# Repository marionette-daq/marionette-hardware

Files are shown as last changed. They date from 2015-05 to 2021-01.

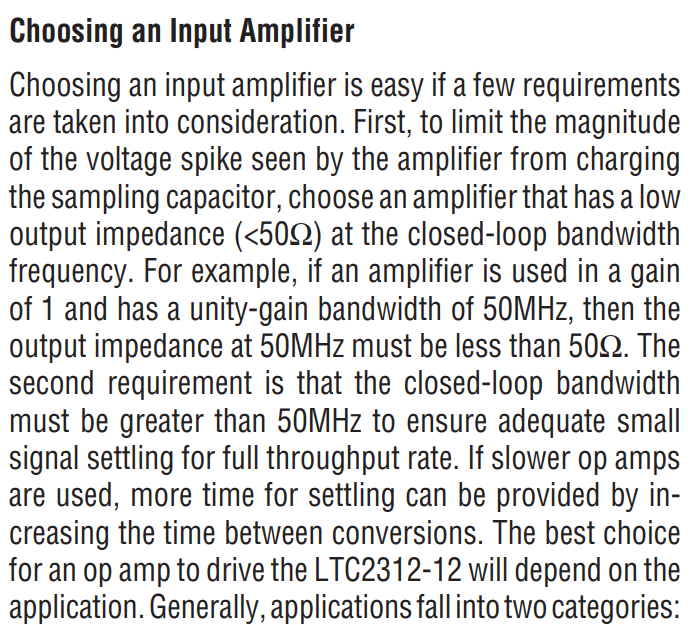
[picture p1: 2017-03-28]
current_amplifier/design/pictures/buffer_amp_requirements.png.png

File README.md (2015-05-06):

# Marionette Data Acquisition System

This repo contains the open source hardware used in the Marionette data acquisition system.
Click here to go to the [Wiki](https://github.com/marionette-daq/marionette-hardware/wiki)
## Marionette Specs

- TBD

## Marionette HW Description

Marionette provides these perifherals:

|Perifheral|Qty|
|---|---|
|GPIO|60|
|ADC|15|
|DAC|5|
|I2C|2|
|CAN 2.0B|1|
|SPI|1|
|SD Card|1|

## Other
* Board is designed in EAGLE 7.x and are fabricated using OSH Park's 4 layer service
* [BOM](https://github.com/marionette-daq/marionette-hardware/blob/master/mBOM.xlsx?raw=true) is available as an .XLSX file

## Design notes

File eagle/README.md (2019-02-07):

<h1 id="fab-header"> "Marionette" ("DK") PCB Manufacturing ("fab") Information </h1>
<h1 id="assembly-header"> APDM "Marionette" ("DK") PCB Assembly ("PCBA") Information </h1>

# Overview

### CURRENT PCB NAME AND VERSION: "DK-2.2"
### CURRENT PCBA NAME AND VERSION: "DK-2.2"

Ver   | Date       | Notes
------|------------|------------------------------------------------------------
2.0   | 2015-12-01 | Marionette V2.0 
2.1   | 2016.05.26 | Marionette V2.1 
2.2   | 2019.02.01 | Marionette V2.2 

## Description

The Marionette PCBA is 150 x 95 mm four layer PCB with a mix of through-hole
and SMT components on the top side.  

<h1 class="pdf" id="fab-pdf:fab" task="pdf:fab"/>

<h1 class="pdf" id="assembly-pdf:assembly" task="pdf:assembly"/>

<h1 id="assembly-images"> 
</h1>




Images of the Marionette v2.2

<h1 id="fab-info"> 
Printed Circuit Board (PCB) Fabrication information 
</h1>

- 4 layers, 1.59 mm (0.0625 inches) thick PCB 
- PCB bounding box size is 150 mm x 95 mm (5.9 x 3.74 inches)
- Minimum Trace / Space design rules
   - Outer layers: 0.15 mm (6.0 mil)
   - Inner layers: 0.2000 mm (7.8 mil)
- Outer dimension router tolerance: +/- 0.127 mm (0.005 in)
- Hole placement tolerance: .075 mm (+/-0.003 inch)
- Inner tab routed slot tolerance: +/- 0.127 mm (5 mil)
- Plated/Un-plated holes
  - There are 7 un-plated holes
  - There are 1304 plated through holes
  - PTH minimum diameter: 0.254 mm (10 mil)
  - PTH minimum annulus: 0.127 mm (5 mil) radius
- Plated slots
  - There 0 interior plated slots
- There are 3 fiducials
   - 3 on the top layer
- Panel tabs
   - Board does not yet have marked tabs. 
   - (Ignore for now) Do NOT place tabs anywhere else.
- Controlled impedance
   - While this board is no controlled impedance, the stackup is critical
     for performance of high speed signals (USB 2.0 high speed @ 480 Mbps)
- If not otherwise specified, build to IPC 6012 Class 2 or better.

## Materials

- Board thickness is 1.59 mm (0.063 inch) +/- 2 mil)
- Isola 370HR or equivalent
   - Laminate material MUST be Isola 370HR or equivalent (including an equivalent Dk).
   - Must have a flammability rating of at least V-0 (according to UL 94).
   - Must have a Dielectric Constant of ~ 4.5 at 1 MHz.
- Board Surface treatment should be ENIG, althogh immersion Silver is acceptable.
- White silkscreen on top and bottom surface
- Taiyo PSR-4000 or equivalent green soldermask on top and bottom

## Stack up

- Top and bottom prepreg thickness **MUST** be 0.111mm (4.4 mil) because of microstrips.

| Layer         | Thickness           | Notes                                        |
|---------------|---------------------|----------------------------------------------|
| Top Copper    | 0.043 mm /  1.7 mil |  Layer 1 foil, 1 oz Cu after plating         |
| prepreg       | 0.111 mm /  4.4 mil |  Prepreg Isola 370HR - 2x "1080"             |
| Layer 2       | 0.036 mm /  1.4 mil |  Layer 2 foil, 1 oz Cu                       |
| Core          | 1.207 mm / 47.5 mil |  Core Isola 370HR                            |
| Layer 3       | 0.036 mm /  1.4 mil |  Layer 3 foil, 1 oz Cu                       |
| prepreg       | 0.111 mm /  4.4 mil |  Prepreg Isola 370HR - 2x "1080"             |
| Bottom Copper | 0.043 mm /  1.7 mil |  Layer 4 foil, 1 oz copper after plating     |
| **Total Stackup** | **1.588 mm / 62.5 mil** |                                              |

## Array / Panel Information

- Coordinate with Contract Manufacturer (CM) for optimal size of this panel
- If no feedback from CM, then:
   - Panelize single board into apropriate sized array. Example: 5 x 3 array.
   - Use only "TAB" locations for attachment tabs
   - Use a ~ 6 mm (0.25 in) frame around the entire outside panel.

## Fabrication Files

### PCB Artwork

| Filename              | Notes                                         |
| --------------------- | --------------------------------------------- |
| marionette.outline.gbx      | RS274X file for the dimension (outline) layer |
| marionette.milling.gbx      | RS274X file for internal milling              |
| marionette.xln              | Excellon drill file                           |
| marionette.topsilk.gbx      | RS274X file for the top silkscreen            |
| marionette.topmask.gbx      | RS274X file for the top soldermask            |
| marionette.toplayer.gbx     | RS274X file for the top copper layer          |
| marionette.layer2.gbx       | RS274X file for the layer 2 copper            |
| marionette.layer3.gbx       | RS274X file for the layer 3 copper            |
| marionette.bottomlayer.gbx  | RS274X file for the bottom copper layer       |
| marionette.bottommask.gbx   | RS274X file for the bottom soldermask         |
| marionette.bottomsilk.gbx   | RS274X file for the bottom silkscreen         |

### Documentation

| Filename            | Notes                                   |
| ------------------- | --------------------------------------- |
| marionette.doc.gbx        | RS274X file for documentation           |
| marionette.ipc            | IPC-D-356 netlist and board layout file |

### Stencils

| Filename                 | Notes                                |
| ------------------------ | ------------------------------------ |
| marionette.toppaste.gbx        | RS274X file for solder paste stencil |

<h1 id="assembly-info">

Printed Circuit Board Assembly (PCBA) Information
</h1>

## Assembly info

- Assemble to IPC Class 2 or better
- Assemble with leaded solder 
- Aqueous flux and wash.
- There are 9 placements of 4 different components that require through hole soldering:
   - 6x Hirose ZX80-B-5SA microUSB vertical connectors (J5101 - J5106)
   - 1x CUI PJ-047AH 5.5mm x 2.1mm barrel power connector (J5001)
   - 1x Hirose ZX62D-B-5P8 USB micro connector (CF5101)
   - 1x FCI 73725-0110BLF USB Type-A vertical RA connector (J5107
- The J22 ZX62D-B-5P8 made by Hirose.  This is a hybrid through hole and SMT part.
**Beware solder ingress from J22 shield pins into the USB chamber.**
If there is solder ingress into the connector, please use a micro B USB
female connector to press into the J22 and clear the excess solder.

## Assembly Files

### Mounting location files

| Filename             | Description                                 |
| -------------------- | ------------------------------------------- |
| marionette.mnt    | Pick and place locations for components     |

### Standard netlist/layout files

Not ready yet

| Filename             | Description                             |
| -------------------- | --------------------------------------- |
| marionette.ipc         | IPC-D-356 netlist and board layout file |

### Stencils

| Filename                       | Notes                                |
| ------------------------------ | ------------------------------------ |
|     marionette.toppaste.gbx          | RS274X file for solder paste stencil |

### Bill of materials

There is the option of populating the 26 MHz clock with a TCXO or an XTAL
with associated filter networks.  The ATTRIBUTE: 'NO_MNT' indicates whether the
component should be populated.  

| Filename                    | Description                        |
| --------------------------- | ---------------------------------- |
| bom/marionette_bom.xls           | BOM with TCXO/XTAL population variants |

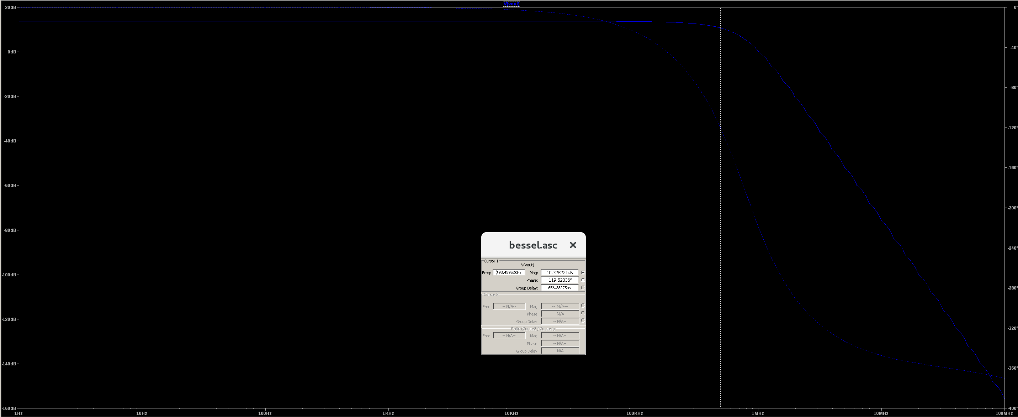
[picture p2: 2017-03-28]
current_amplifier/design/pictures/bessel_sim.png

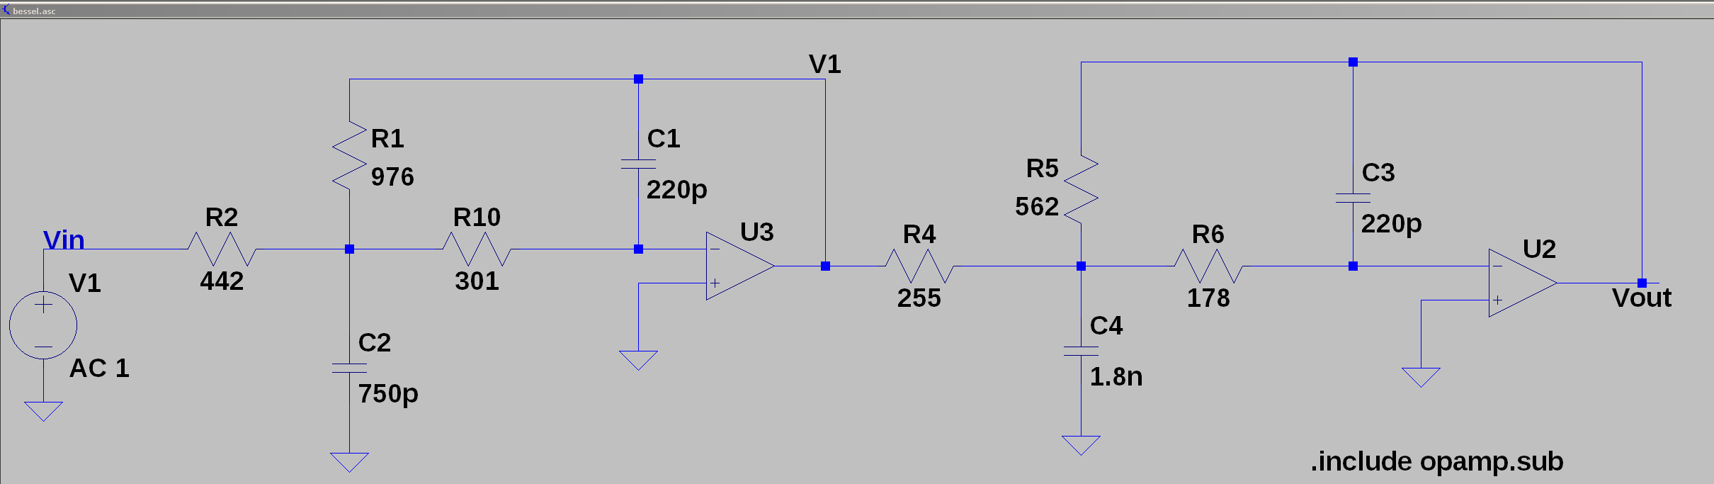
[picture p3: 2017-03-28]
current_amplifier/design/pictures/bessel_filter_lt.png

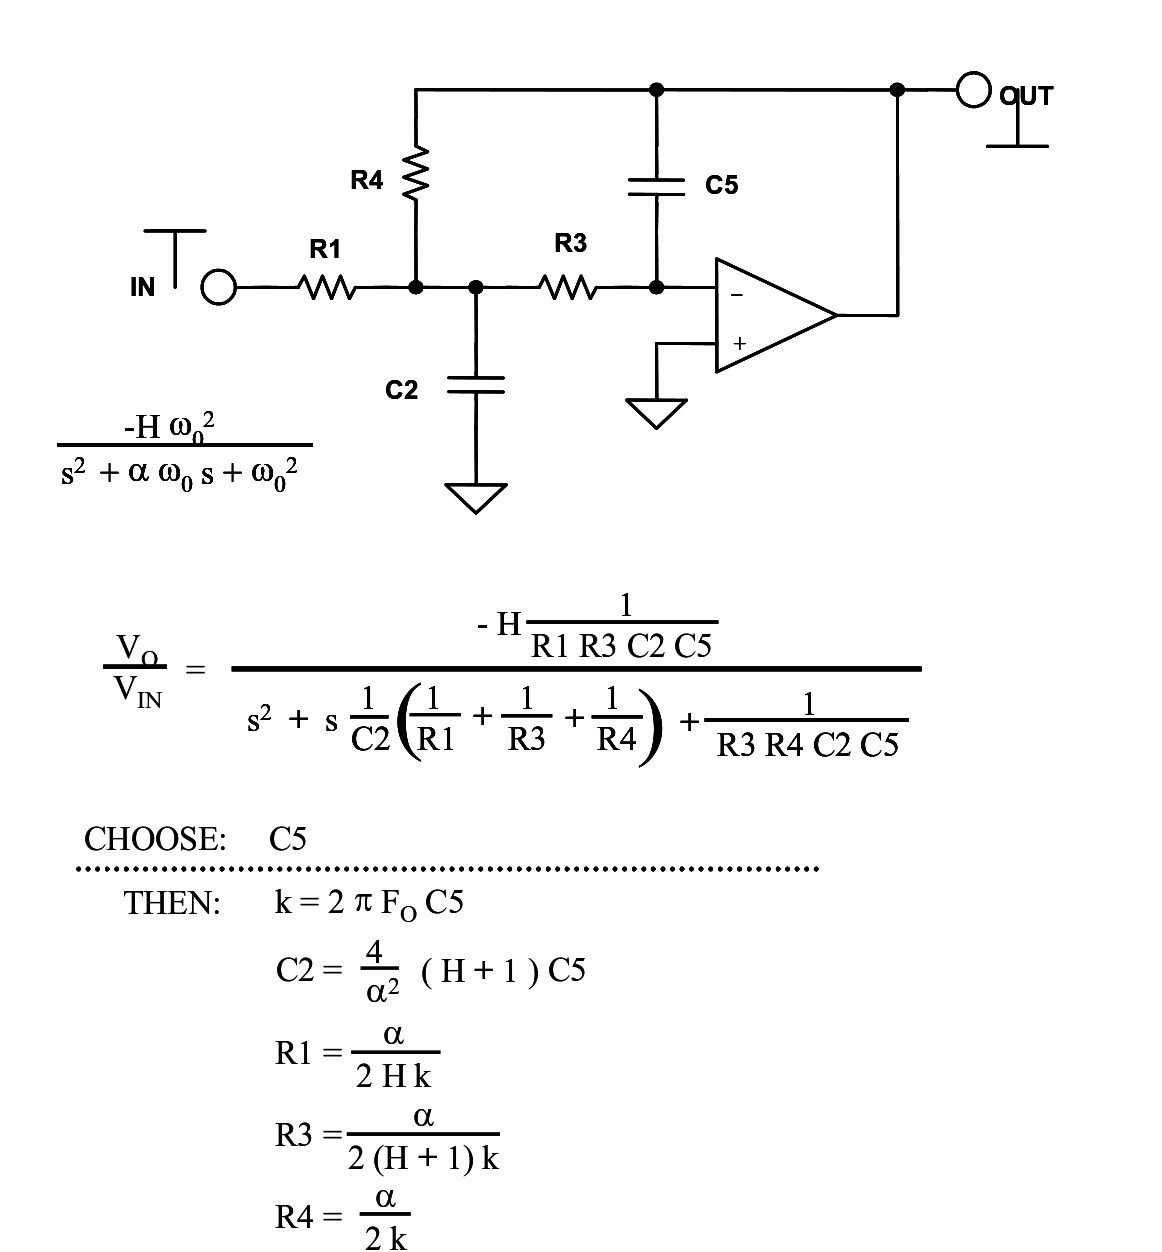
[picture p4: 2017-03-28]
current_amplifier/design/pictures/MFB.png

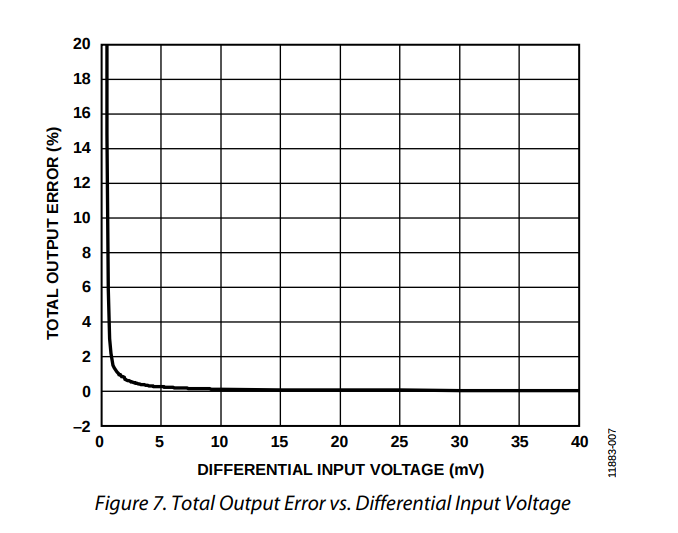
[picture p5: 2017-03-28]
current_amplifier/design/pictures/Error_vs_Diff_Input_Voltage.png

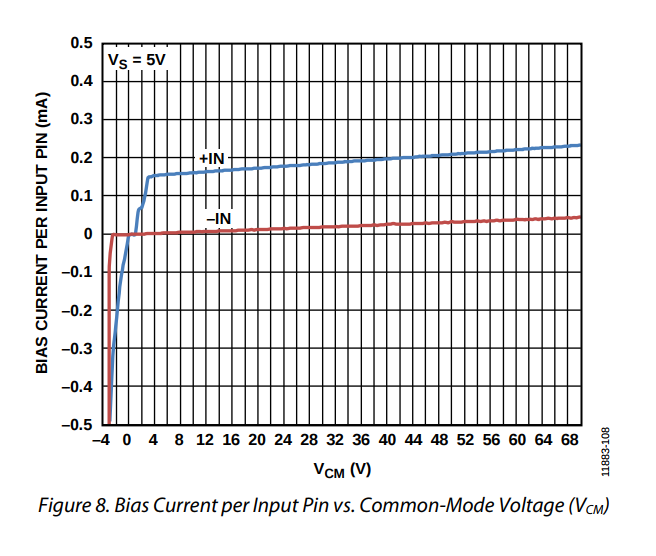
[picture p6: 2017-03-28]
current_amplifier/design/pictures/bias_current.png

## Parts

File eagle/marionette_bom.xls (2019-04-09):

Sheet: BOM
Bill Of Materials for Marionette
Modified: 2019.01.24
source file: marionette.sch
Variant: NA
PCB version 2.2
BOM revision 1
Cnt | REFs | Manf | PN | P/DNP (variant) | Desc | Vendor | Vendor-PN | Generic | Note
1 | C1 | Murata | GRM1555C1H6R8CA01D | P | Chip Capacitor, 6.8p, +-0.5pF, C0G/NP0, 50V, 0402 | Digikey | 490-5949-1-ND | Y
4 | C27, C30, C114, C154 | Murata | GRM1555C1H100JA01D | P | Chip Capacitor, 10p, +-5%, C0G/NP0, 50V, 0402 | Digikey | 490-5921-1-ND | Y
1 | C3 | Murata | GRM1555C1H330JA01D | P | Chip Capacitor, 33p, +-5%, C0G/NP0, 50V, 0402 | Digikey | 490-5936-1-ND | Y
1 | C42 | Murata | GRM1555C1H101JA01D | P | Chip capacitor, 100pF, 5%, 50V, C0G/NP0, 0402 | Digikey | 490-5922-1-ND | Y
30 | C50, C51, C52, C57, C59, C60, C61, C62, C63, C64, C67, C68, C69, C70, C71, C72, C75, C76, C77, C78, C79, C80, C49, C53, C54, C58, C65, C66, C73, C74 | Murata | GRM1555C1H102JA01D | P | Chip Capacitor, 1n, +-5%, 50V, C0G/NP0, 0402 | Digikey | 490-3244-1-ND | Y
6 | C29, C33, C101, C117, C142,C143 | Murata | GRM155R71E103KA01D | P | Chip capacitor, 10nF, 10%, 25V, X7R, 0402 | Digikey | 490-1312-1-ND | Y
1 | C33 | Murata | GRM155R71E103KA01D | P (XTAL/TCXO) | Chip capacitor, 10nF, 10%, 25V, X7R, 0402 | Digikey | 490-1312-1-ND | Y
2 | C41, C45 | TDK | CGA2B3X5R1H683K050BB | P | Chip capacitor, 68nF, 10%, 50V, X7R, 0402 | Digikey | 445-12211-1-ND | Y
43 | C2, C4, C7, C8, C9, C10, C11, C12, C13, C14, C15, C16, C17, C18, C19, C20, C21, C24, C25, C36, C37, C39, C43, C44, C47, C48, C86, C90, C91, C92, C97, C98, C99, C121, C126, C137, C140, C151, C152, C31, C103, C109, C110, C111 | Murata | GRM155R61E104KA87D | P | Chip capacitor, 100nF, 10%, 25V, X5R, 0402 | Digikey | 490-5920-1-ND | Y
3 | C40, C102, C113 | Walsin | 0402B104K500CT | P | Chip capacitor, 100nF, 10%, 50V, X7R, 0402 | Digikey | 1292-1176-1-ND | Y
10 | C23,C28,C32,C55,C56,C81,C82,C83,C85,C93 | Murata | GRM155R61A105KE15D | P | Chip capacitor, 1.0uF, 10%, 10V, X5R, 0402 | Digikey | 490-3890-1-ND | Y
21 | C5, C22, C26, C38, C87, C88, C89, C94, C96, C118, C120, C127, C138, C139, C145, C146, C153, C100, C104, C105, C112 | Murata | GRM21BR61E475KA12L | P | Chip Capacitor, 4.7u, 10%, 25V, X5R, 0805 | Digikey | 490-3335-1-ND | Y
5 | C46, C107, C108, C115, C116 | Murata | GRM21BR61H475KE51L | P | Chip Capacitor, 4.7u, 10%, 50V, X5R, 0805 | Digikey | 490-10751-1-ND | Y
1 | D3 | MCC | BAS40-TP | P | Schottky Diode, Vf = 1.0V, Vr = 40V, Imax = 200mA, SOT23-3 | Digikey | BAS40TPMSCT-ND | N
17 | D1,D2,D4,D5,D6,D7,D8,D9,D10,D11,D12,D13,D14,D15,D16,D17,D18 | Onsemi | ESD8006MUTAG | P | TVS protection Diode array, Vclamp = (5.5V, 8.4V), UDFN-8 3.3mm x 1.0mm | Digikey | ESD8006MUTAGOSCT-ND | N
4 | D20, D21, D22, D24 | Comchip | CDBA140SL-HF | P | Schottky Diode, Vr = 40V, Vf = 330mV, Imax = 1A DO-214AC/SMA | Digikey | 641-1762-1-ND | N
1 | D27 | Onsemi | MBRS260T3G | DNP | Schottky Diode, Vr = 60V, Imax = 2A, DO-214AA/SMB | Digikey | MBRS260T3GOSCT-ND | N | This diode is not required for most applications.
3 | D19, D25, D26 | Vishay | VSKY05201006-G4-08 | P | Schottky Diode, Vr = 20V, Imas = 500mA, 0402 package | Digikey | VSKY05201006-G4-08GICT-ND | N
1 | F1 | Bel Fuse | C1Q2 | P | Chip Fuse, 2A, 1206 | Digikey | 507-1080-1-ND | N
1 | J4 | JST | B2B-PH-K-S(LF)(SN) | P | JST 2 pin connector, 2A rating | Digikey | 455-1704-ND | N
1 | JP2 | Harwin | M20-9980445 | P | Header, 2 x 4, unshrouded, vert, TH, 100mil pitch | Digikey | 952-2122-ND | Y
3 | J3,J8,J9 | Sullins Connectivity | SBH11-PBPC-D20-ST-BK | P | IDC connector 40 pin, shrouded, keyed , 2 x 20 pin, 100mil | Digikey | S9175-ND | Y
1 | J5 | CUI | PJ-047AH | P | Jack, male, 5A, 16VDC, TH, Shielded, Internal Switch, (for 2.1mm pin Dia. 5.5mm hole dia. Plug) | Digikey | CP-047AH-ND | N
1 | J12 | Sullins Connectivity | SBH11-PBPC-D10-ST-BK | P | IDC connector 20 pin, shrouded, keyed, 2 x 10 pin, 100mil | Digikey | S9172-ND | Y
1 | J13 | CNC Tech | 3220-10-0300-00 | P | JTAG header, shrouded, keyed 2 x 5 pin. 50mil pitch | Digikey | 1175-1629-ND | Y
1 | J14 | Hirose | DM3D-SF | P | Micro SD card holder, push-pull manual extraction, no ejection mech. | Digikey | HR1941CT-ND | N
1 | J22 | Hirose | ZX-62D-B-5P8 | P | Connector, USB Micro B, surface mount + TH, RA | Digikey | H11610CT-ND | N
2 | JP1,JP5 | Sullins Connectivity | PRPC040SAAN-RC | DNP | Header, 1x2, male, breakaway, unshrouded, TH, 100mil 1 x 40: cut to 1x2 | Digikey | S1011EC-40-ND | Y
1 | JP3 | Sullins Connectivity | PRPC040SAAN-RC | P | Header, 1x3, male, breakaway, unshrouded, TH, 100mil 1 x 40: cut to 1x3 | Digikey | S1011EC-40-ND | Y
1 | JP9 | Sullins Connectivity | PRPC002DAAN-RC | P | Header, 2x2, male, unshrouded, TH, 100mil | Digikey | S2011EC-02-ND | Y
1 | J15 | Wurth | 398800302 | P | Euroterminal, 2 terminal, 5.08mm | Digikey | WM4393-ND | Y
1 | L1 | Murata | 1255AY-6R8M=P3 | P | Fixed Inductor, 6.8uH, Shielded, 3.4A, .043 ohms, 6.3mm x 6.3mm | Digikey | 490-14063-1-ND | N
1 | L2 | Bournes | SRN3015-2R2M | P | Fixed Inductor, shielded, 2.2uH, 20%, .072 ohms, 1.8A, 3.0mm x 3.0mm | Digikey | SRN3015-2R2MCT-ND | N
6 | LED1,LED2,LED3,LED4,LED6,LED8 | Wurth | 150060VS75000 | P | LED, Green, 20mA, diffused lens, 0603 | Digikey | 732-4980-1-ND | N
1 | LED5 | Rohm | SMLV56RGB1W1 | P | LED, RGB, 20mA each channel, 6SMD | Digikey | 846-1000-1-ND | N
1 | Q3 | Alpha Omega | AO3419 | P | PFET, 20V, 3.5A, SOT23-3 | Digikey | 785-1013-1-ND | N
22 | R17, R30, R66, R70, R79, R80, R81, R82, R83, R84, R85, R86, R87, R88, R89, R90, R91, R92, R93, R94, R110 | Samsung | RC1005J000CS | P | Thick Film Chip Resistor, 0 ohm, jumper, 0402 | Digikey | 1276-3480-1-ND | Y
1 | R17 | Samsung | RC1005J000CS | P (XTAL/TCXO) | Thick Film Chip Resistor, 0 ohm, jumper, 0402 | Digikey | 1276-3480-1-ND | Y
1 | R104 | Yageo | RC0603JR-070RL | P | Thick Film Chip Resistor, 0 ohm, jumper, 0603 | Digikey | 311-0.0GRCT-ND | Y
1 | R29 | Yageo | RC0402FR-07120RL | P | Thick Film Chip Resistor, 120 ohm, 1%, 0402 | Digikey | 311-120LRCT-ND | Y
2 | R13,R14 | Yageo | RC0402FR-07510RL | P | Thick Film Chip Resistor, 510 ohm, 1%, 0402 | Digikey | 311-510LRCT-ND | Y
1 | R12 | Yageo | RC0402FR-07620RL | P | Thick Film Chip Resistor, 620 ohm, 1%, 0402 | Digikey | 311-620LRCT-ND | Y
9 | R19, R22, R23, R24, R25, R27, R71, R105, R111 | Yageo | RC0402FR-071KL | P | Thick Film Chip Resistor, 1k ohm, 1%, 0402 | Digikey | 311-1.00KLRCT-ND | Y
4 | R6,R7,R202,R203 | Yageo | RC0402FR-074K7L | P | Thick Film Chip Resistor, 4.7k ohm, 1%, 0402 | Digikey | 311-4.7KLRCT-ND | Y
30 | R31, R32, R33, R34, R35, R36, R39, R40, R41, R42, R43, R44, R45, R46, R47, R48, R49, R50, R51, R52, R53, R54, R55, R56, R57, R58, R59, R60, R61, R62 | Yageo | RC0402FR-077K5L | P | Thick Film Chip Resistor, 7.5k ohm, 1%, 0402 | Digikey | 311-7.50KLRCT-ND | Y
1 | R201 | Yageo | RC0402FR-078K06L | P | Thick Film Chip Resistor, 8.06k ohm, 1%, 0402 | Digikey | 311-8.06KLRCT-ND | Y
13 | R1, R15, R16, R20, R37, R38, R63, R64, R72, R75, R76, R77, R109 | Rohm | MCR01MRTF1002 | P | Thick Film Chip Resistor, 10k, 1%, 0402 | Digikey | RHM10.0KCDCT-ND | Y
1 | R4 | Yageo | RC0402FR-0712KL | P | Thick Film Chip Resistor, 12k, 1%, 0402 | Digikey | 311-12.0KLRCT-ND | Y
1 | R69 | Yageo | RC0402FR-0720KL | P | Thick Film Chip Resistor, 20k, 1%, 0402 | Digikey | 311-20.0KLRCT-ND | Y
1 | R28 | Yageo | RC0402FR-0727K4L | P | Thick Film Chip Resistor, 27.4k, 1%, 0402 | Digikey | 311-27.4KLRCT-ND | Y
7 | R5,R8,R9,R10,R11,R67,R78 | Yageo | RC0402FR-0747KL | P | Thick Film Chip Resistor, 47k ohm, 1%, 0402 | Digikey | 311-47.0KLRCT-ND | Y
4 | R18,R65,R74,R108 | Rohm | MCR01MRTF1003 | P | Thick Film Chip Resistor, 100k, 1%, 0402 | Digikey | RHM100KCDCT-ND | Y
1 | R3 | Panasonic | ERJ-2RKF4993X | P | Thick Film Chip Resistor, 499k ohm, 1%, 0402 | Digikey | P499KLCT-ND | Y
1 | R73 | Yageo | RC0402FR-07562KL | P | Thick Film Chip Resistor, 562k ohm, 1%, 0402 | Digikey | 311-562KLRCT-ND | Y
4 | R2, R21,R96, R204 | Rohm | MCR01MRTF1004 | P | Thick Film Chip Resistor, 1.0Meg, 1%, 0402 | Digikey | RHM1.00MCDCT-ND | Y
2 | SW3,SW4 | TE | FSM1LPSTR | P | Momentary Tactile Switch, SMD, Vertical | Digikey | 450-2156-1-ND | N
2 | U1,U15 | NXP | 74HC4066D,653 | P | Analog Switch, quad channel, 95 ohm on resistance | Digikey | 568-1462-1-ND | N
2 | U3,U40 | Analog | ADP160AUJZ-3.3-R7 | P | LDO, 3.3V fixed output, Imax = 150mA, Vdropout = 195mV, SOT23-5 | Digikey | ADP160AUJZ-3.3-R7CT-ND | N
1 | U4 | TI | DAC124S085CIMM/NOPB | P | DAC, 12 bit, Quad channel, 10 MSOP, SPI | Digikey | DAC124S085CIMM/NOPBCT-ND | N
1 | U5 | Maxim | MAX3051ESA+T | P | CAN transceiver, SO-8 | Digikey | MAX3051ESA+CT-ND | N
4 | U7,U8,U9,U10 | TI | LMV344IDR | P | Op amp, quad channel, 1Mhz, SOIC-14 | Digikey | 296-20925-1-ND | N
1 | U2 | Ablic | S-1011N42-M6T1U4 | P | Delay Circuit IC/ Voltage Detector, SOT23-6 | Digikey | 1662-2776-1-ND | N
1 | U6 | Analog | LTC3114IFE-1 | P | Synchronous Buck Boost, Vin = (40V, 2.2V), 1A, TSSOP-16-EP | Digikey | LTC3114IFE-1#PBF-ND | N
1 | U11 | STMicro | STM32F427IIT6 | P | ARM Cortex-M4 32b MCU+FPU, LQFP-176 | Digikey | 497-14051-ND | N
1 | U12 | Microchip | MCP73855T-I/MF | P | IC Controller Li-Ion/Li-Poly Charge Mgmt Controller, DFN-10 | Digikey | MCP73855T-I/MFCT-ND | N
1 | U14 | MicroChip | USB3320C-EZK-TR | P | USB PHY, USB 2.0 multi-frequency, QFN-32 5mm x 5mm | Digikey | USB3320C-EZK-CT-ND | N
1 | U17 | TI | LM3671MF-3.3/NOPB | P | Buck converter, 2Mhz, 600mA, SOT23-5 | Digikey | LM3671MF-3.3/NOPBCT-ND | N
1 | U140 | Onsemi | LM317LDR2G | P | Linear Regulator, SOIC-8, | Digikey | LM317LDR2GOSCT-ND | Y
1 | U41 | Analog | ADP160AUJZ-1.8-R7 | P | LDO, 1.8V fixed output, Imax = 150mA, Vdropout = 195mV, SOT23-5 | Digikey | ADP160AUJZ-1.8-R7CT-ND | N
1 | X1 | Abracon | ABS07-32.768KHZ-T | P | Crystal, 32.7680kHz, 12.5pF, 20ppm | Digikey | 535-9542-1-ND | N
1 | TCXO1 | Connor-Winfield | D32G-026.0M | P (XTAL/TCXO) | TCXO, 26.000Mhz, ±500ppb, sine output | Digikey | CW662CT-ND | N
307
 | Notes:
 | Rev 0: TCXO/XTAL variants shown on the BOM
 | Rev 1: BOM made exclusively for TCXO

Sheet: DIGIKEY-ORDER
1 | , | 490-5949-1-ND | , | C1
4 | , | 490-5921-1-ND | , | C27, C30, C114, C154
#REF! | , | #REF! | , | #REF!
#REF! | , | #REF! | , | #REF!
1 | , | 490-5936-1-ND | , | C3
1 | , | 490-5922-1-ND | , | C42
30 | , | 490-3244-1-ND | , | C50, C51, C52, C57, C59, C60, C61, C62, C63, C64, C67, C68, C69, C70, C71, C72, C75, C76, C77, C78, C79, C80, C49, C53, C54, C58, C65, C66, C73, C74
6 | , | 490-1312-1-ND | , | C29, C33, C101, C117, C142,C143
1 | , | 490-1312-1-ND | , | C33
43 | , | 490-5920-1-ND | , | C2, C4, C7, C8, C9, C10, C11, C12, C13, C14, C15, C16, C17, C18, C19, C20, C21, C24, C25, C36, C37, C39, C43, C44, C47, C48, C86, C90, C91, C92, C97, C98, C99, C121, C126, C137, C140, C151, C152, C31, C103, C109, C110, C111
#REF! | , | #REF! | , | #REF!
10 | , | 490-3890-1-ND | , | C23,C28,C32,C55,C56,C81,C82,C83,C85,C93
21 | , | 490-3335-1-ND | , | C5, C22, C26, C38, C87, C88, C89, C94, C96, C118, C120, C127, C138, C139, C145, C146, C153, C100, C104, C105, C112
#REF! | , | #REF! | , | #REF!
#REF! | , | #REF! | , | #REF!
#REF! | , | #REF! | , | #REF!
1 | , | BAS40TPMSCT-ND | , | D3
17 | , | ESD8006MUTAGOSCT-ND | , | D1,D2,D4,D5,D6,D7,D8,D9,D10,D11,D12,D13,D14,D15,D16,D17,D18
1 | , | 507-1080-1-ND | , | F1
1 | , | 952-2122-ND | , | JP2
3 | , | S9175-ND | , | J3,J8,J9
1 | , | CP-047AH-ND | , | J5
1 | , | S9172-ND | , | J12
1 | , | 1175-1629-ND | , | J13
1 | , | HR1941CT-ND | , | J14
1 | , | H11610CT-ND | , | J22
2 | , | S1011EC-40-ND | , | JP1,JP5
1 | , | S1011EC-40-ND | , | JP3
1 | , | S2011EC-02-ND | , | JP9
1 | , | 490-14063-1-ND | , | L1
1 | , | SRN3015-2R2MCT-ND | , | L2
6 | , | 732-4980-1-ND | , | LED1,LED2,LED3,LED4,LED6,LED8
1 | , | 846-1000-1-ND | , | LED5
#REF! | , | #REF! | , | #REF!
#REF! | , | #REF! | , | #REF!
1 | , | 785-1013-1-ND | , | Q3
#REF! | , | #REF! | , | #REF!
22 | , | 1276-3480-1-ND | , | R17, R30, R66, R70, R79, R80, R81, R82, R83, R84, R85, R86, R87, R88, R89, R90, R91, R92, R93, R94, R110
1 | , | 1276-3480-1-ND | , | R17
1 | , | 311-0.0GRCT-ND | , | R104
#REF! | , | #REF! | , | #REF!
1 | , | 311-120LRCT-ND | , | R29
#REF! | , | #REF! | , | #REF!
2 | , | 311-510LRCT-ND | , | R13,R14
1 | , | 311-620LRCT-ND | , | R12
#REF! | , | #REF! | , | #REF!
9 | , | 311-1.00KLRCT-ND | , | R19, R22, R23, R24, R25, R27, R71, R105, R111
4 | , | 311-4.7KLRCT-ND | , | R6,R7,R202,R203
30 | , | 311-7.50KLRCT-ND | , | R31, R32, R33, R34, R35, R36, R39, R40, R41, R42, R43, R44, R45, R46, R47, R48, R49, R50, R51, R52, R53, R54, R55, R56, R57, R58, R59, R60, R61, R62
1 | , | 311-8.06KLRCT-ND | , | R201
13 | , | RHM10.0KCDCT-ND | , | R1, R15, R16, R20, R37, R38, R63, R64, R72, R75, R76, R77, R109
7 | , | 311-47.0KLRCT-ND | , | R5,R8,R9,R10,R11,R67,R78
#REF! | , | #REF! | , | #REF!
4 | , | RHM100KCDCT-ND | , | R18,R65,R74,R108
#REF! | , | #REF! | , | #REF!
#REF! | , | #REF! | , | #REF!
1 | , | 311-562KLRCT-ND | , | R73
4 | , | RHM1.00MCDCT-ND | , | R2, R21,R96, R204
2 | , | 450-2156-1-ND | , | SW3,SW4
2 | , | 568-1462-1-ND | , | U1,U15
#REF! | , | #REF! | , | #REF!
2 | , | ADP160AUJZ-3.3-R7CT-ND | , | U3,U40
1 | , | DAC124S085CIMM/NOPBCT-ND | , | U4
1 | , | MAX3051ESA+CT-ND | , | U5
#REF! | , | #REF! | , | #REF!
4 | , | 296-20925-1-ND | , | U7,U8,U9,U10
1 | , | 497-14051-ND | , | U11
1 | , | MCP73855T-I/MFCT-ND | , | U12
1 | , | USB3320C-EZK-CT-ND | , | U14
1 | , | LM3671MF-3.3/NOPBCT-ND | , | U17
1 | , | ADP160AUJZ-1.8-R7CT-ND | , | U41
1 | , | 535-9542-1-ND | , | X1
#REF! | , | #REF! | , | #REF!
1 | , | CW662CT-ND | , | TCXO1

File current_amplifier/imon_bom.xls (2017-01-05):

Bill Of Materials for Current Monitor Board
Modified: 2016.12.28
source file: imon.sch
Variant: NA
PCB version 1.0
BOM revision 1
Cnt | APDM-PN | REFs | Manf | PN | P/DNP | Desc | Vendor | Vendor-PN | Generic
1 |  | JP1
1 |  | JP2
1 |  | JP4
2 |  | C5, C50 | Murata | GRM1555C1H221JA01D |  | Chip capacitor, 220pF, 5%, 50V, NP0, 0402 | Digikey | 490-1293-1-ND
1 |  | C2 | Murata | GRM1555C1E751JA01D |  | Chip capacitor, 750pF, 10%, 25V, NP0, 0402 | Digikey | 490-6183-1-ND
1 |  | C20 | Murata | GRM155R71H182KA01D |  | Chip capacitor, 1.8nF, 10%, 50V, X7R, 0402 | Digikey | 490-3246-1-ND
1 |  | C1 | Murata | GRM155R71E103KA01D |  | Chip capacitor, 10nF, 10%, 25V, X7R, 0402 | Digikey | 490-1312-1-ND
3 |  | C3, C10, C80 | Murata | GRM155R61E104KA87D |  | Chip capacitor, 100nF, 10%, 25V, X5R, 0402 | Digikey | 490-5920-1-ND
9 |  | C4, C6, C7, C11, C12, C14, C15, C19, C105 | Murata | GRM155R61A105KE15D |  | Chip capacitor, 1.0uF, 10%, 10V, X5R, 0402 | Digikey | 490-3890-1-ND
1 |  | C13 | Murata | GRT21BR61C106KE01L |  | Chip capacitor, 10uF, 10%, 16V, X5R, 0805 | Digikey | 490-12379-1-ND
2 |  | R7, R8 | Stackpole | RNCS0805BKE10R0 |  | 10, 0805, 0.1%, | Digikey | RNCS0805BKE10R0CT-ND
1 |  | R30 | Yageo | RC0402FR-07178RL |  | 178, 0.1%, 0402, 1/16 W, Thin film | Digikey | YAG3011CT-ND
1 |  | R10 | Yageo | RC0402FR-07255RL |  | 255, 1%, 0402, 1/16 W, Thin film | Digikey | YAG3075CT-ND
1 |  | R3 | Yageo | RC0402FR-07301RL |  | 301, 1%, 0402, 1/16 W, Thin film | Digikey | 311-301LRCT-ND
1 |  | R1 | Yageo | RC0402FR-07442RL |  | 442, 1%, 0402, 1/16 W, Thin film | Digikey | YAG3162CT-ND
1 |  | R40 | Yageo | RC0402FR-07562RL |  | 562, 1%, 0402, 1/16 W, Thin film | Digikey | YAG3186CT-ND
1 |  | R4 | Yageo | RC0402FR-07976RL |  | 976, 1%, 0402, 1/16W, Thin film | Digikey | YAG3266CT-ND
1 |  | R18 | Yageo | RC0402FR-071KL |  | 1k, 1%, 0402, 1/16W, Thin film | Digikey | 311-1.00KLRCT-ND
2 |  | R2, R6 | Rohm | MCR01MRTF1002 |  | 10k, 1%, 0402, 1/16W, Thin film | Digikey | RHM10.0KCDCT-ND
1 |  | U4 | Analog | AD8418WBRZ |  | IC current sense op amp | Digikey | AD8418WBRZ-ND
1 |  | D1 | On Semi | ESD8006MUTAG |  | TVS diode, 8-DFN | Digikey | ESD8006MUTAGOSCT-ND
1 |  | U6 | Linear | LTC2312CTS8-12#TRMPBF |  | ADC | Digikey | LTC2312CTS8-12#TRMPBFCT-ND
1 |  | U5 | Microchip | MCP1501T-20E/CHY |  | Reference Voltage, 0.1%, SOT23-6 | Digikey | MCP1501T-20E/CHYCT-ND
1 |  | U2 | Fairchild | FAN4852IMU8X |  | Dual op amp, 9Mhz, 8MSOP | Digikey | FAN4852IMU8XCT-ND

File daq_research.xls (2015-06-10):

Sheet: Sheet1
Device | price | Performance |  |  |  |  |  |  |  |  |  |  |  | languages suported | pc interface | platforms | Website | Optional Names
 |  | Bits |  | Input Voltage Range | Counters | Resolution | GPIO | ADC Channels | DAC Channels | Digital I/O | SPI | I2C | CAN
openDaq | $300.00 | adc | 16 | +/- 12V | 1 | 16bit | x | 8 | 1 | 6 | x | x | x | LabVIEW | USB | Windows | http://www.open-daq.com/productos/opendaq-m | ba-daq-a-daq
 |  | dac | 14 |  |  |  |  |  |  |  |  |  |  | Python |  | Linux |  | ba-donk-a-daq
 |  | sample rate | 20 kS/s |  |  |  |  |  |  |  |  |  |  |  |  | iOS |  | Give me convenience or give me daq
 |  | sample rate to the pc |  |  |  |  |  |  |  |  |  |  |  |  |  |  |  | auto-di-daq-dic
MiniLab1008 | $129.00 | adc | 12 | +/- 10V | 1 | 32bit | x | 8 | 2 | 24 | x | x | x | LabVIEW | USB | Windows | http://www.microdaq.com/measurement_computing/usb_data_acquisition/multifunction/minilab-daq.php | redaq-did?
 |  | dac |  |  |  |  |  |  |  |  |  |  |  |  |  | Vista |  | daq, DAQ!!
 |  | sample rate | 1.2 kS/s |  |  |  |  |  |  |  |  |  |  |  |  | XP SP2 |  | stringDAQ
 |  | sample rate to the pc |  |  |  |  |  |  |  |  |  |  |  |  |  |  |  | stringerDAQ
USB-201 | $99.00 | adc | 12 | +/- 10V | 1 | 32bit | x | 8 | x | 8 | x | x | x | LabVIEW | USB | Windows | http://www.microdaq.com/measurement_computing/usb_data_acquisition/multifunction/usb-200/usb-201-daq.php | diDAQdic
 |  | dac |  |  |  |  |  |  |  |  |  |  |  | DAQ Flex |  | Linux |  | Unity
 |  | sample rate | 100 kS/s |  |  |  |  |  |  |  |  |  |  |  |  | iOS |  | UnityDAQ
 |  | sample rate to the pc |  |  |  |  |  |  |  |  |  |  |  |  |  | Android |  | ODB (Open Daq Board)
USB-202 | $149.00 | adc | 12 | +/- 10V | 1 | 32bit | x | 8 | 2 | 8 | x | x | x | Universal Library | USB | Windows | http://www.microdaq.com/measurement_computing/usb_data_acquisition/multifunction/usb-200/usb-202-daq.php | Method DAQ
 |  | dac |  |  |  |  |  |  |  |  |  |  |  | DAQ Flex |  | Linux |  | daqstone
 |  | sample rate | 100 kS/s |  |  |  |  |  |  |  |  |  |  | LabVIEW |  | Android |  | daqueen
 |  | sample rate to the pc |  |  |  |  |  |  |  |  |  |  |  |  |  | iOS |  | one eyed DAQ (Our eye is on being best)
USB-1208FS-Plus | $399.00 | adc | 12 | +/- 20V | 1 | 32bit | x | 8 | 2 | 16 | x | x | x | MATLAB | USB | Windows | http://www.mccdaq.com/usb-data-acquisition/USB-1208FS-Plus.aspx | EmporerDAQ
 |  | dac | 12 |  |  |  |  |  |  |  |  |  |  |  |  | Android 3.1 |  | conceitedDAQ
 |  | sample rate | 50 kS/s |  |  |  |  |  |  |  |  |  |  | LabVIEW |  | Linux |  | DAQ to the Future
 |  | sample rate to the pc |  |  |  |  |  |  |  |  |  |  |  | Universal Library
USB-1208HS | $499.00 | adc | 13 | +/- 10V | 2 | 32bit | x | 8 | 0 | 16 | x | x | x | MATLAB | USB | Windows | http://www.mccdaq.com/usb-data-acquisition/USB-1208HS.aspx
 |  | dac |  |  |  |  |  |  |  |  |  |  |  | Universal Library
 |  | sample rate | 1 MS/s |  |  |  |  |  |  |  |  |  |  | LabVIEW
 |  | sample rate to the pc
LabJack U3-LV | $108.00 | adc | 12 | 0-3.6V | 2 | 32bit | 16 (flexible) | 16 (up to) | 2 | 16(up to) | Y | Y | x | Universal Library | USB | Windows | http://labjack.com/u3
 |  | dac | 10 |  |  |  |  |  |  |  |  |  |  | LabView |  | Mac Osx
 |  | sample rate |  |  |  |  |  |  |  |  |  |  |  | MATLAB
 |  | sample rate to the pc |  |  |  |  |  |  |  |  |  |  |  | Python
LabJack U3-HV | $114.00 | adc | 12 | +/- 10V | 2 | 32bit | 16 (flexible) | 16 (up to) | 2 | 16(up to) | y | y | x | Universal Library | USB |  | http://labjack.com/u3
 |  | dac | 10 |  |  |  |  |  |  |  |  |  |  | LabVIEW
 |  | sample rate |  |  |  |  |  |  |  |  |  |  |  | MATLAB
 |  | sample rate to the pc |  |  |  |  |  |  |  |  |  |  |  | Python
NI USB-6211 | $880.00 | adc | 16 | +/- 10V | 2 | 16bit | x | 16 | 2 | Input only | x | x | x | LabVIEW | USB | Windows | http://sine.ni.com/nips/cds/view/p/lang/en/nid/203224
 |  | dac | 16 |  |  |  |  |  |  | 4 |  |  |  | Visual Studio .NET |  | Linux
 |  | sample rate | 250 kS/s |  |  |  |  |  |  | Output Only |  |  |  |  |  | Mac
 |  | sample rate to the pc |  |  |  |  |  |  |  | 4
di-145-usb | $29.00 | adc | 10 | +/- 10V | 1 | 10bit | x | 4 | x | Input only: 2 | x | x | x | WinDAQ | USB | Windows | http://www.dataq.com/products/di-145/index.html?gclid=CKi6oteI7MICFYhafgodUVIAug#nested-tab-2
 |  | dac
 |  | sample rate | 240 S/s
 |  | sample rate to the pc
di-149 | $59.00 | adc | 10 | +/- 10V | 2 | 10bit | x | 8 | x | Input only:4 Ouput only: 4 | x | x | x | WinDAQ | USB | Windows | http://www.dataq.com/resources/pdfs/datasheets/di-149-usb-data-acquisition_ds.pdf
 |  | dac |  |  |  |  |  |  |  |  |  |  |  | Python |  | Linux
 |  | sample rate | 10 kS/s |  |  |  |  |  |  |  |  |  |  | Java |  | Mac
 |  | sample rate to the pc
LabJack U6 | $299.00 | adc | 16 | +/- 10V | 2 | 32bit |  | 14 | 2 | 20 | y | y | x | C/C++ | USB | Windows | http://labjack.com/u6
 |  | dac | 12 |  |  |  |  |  |  |  |  |  |  | .NET |  | Mac
 |  | sample rate | 50 kS/s |  |  |  |  |  |  |  |  |  |  | LabVIEW |  | Linux
 |  |  |  |  |  |  |  |  |  |  |  |  |  | Python
 |  | sample rate to the pc |  |  |  |  |  |  |  |  |  |  |  | MATLAB
 |  | adc
 |  | dac
 |  | sample rate
 |  | sample rate to the pc
 |  | adc
 |  | dac
 |  | sample rate
 |  | sample rate to the pc |  |  |  |  |  |  |  |  |  |  |  |  |  |  |  | 4294967296

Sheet: Sheet2
Category | Di-149 | USB201 | LabJack U3-HV | Minilab1008 | Marionette | USB202 | LabJack U6 | OpenDaq | USB1208FS - Plus
Price | $59.00 | $99.00 | $114.00 | $129.00 | $130 | $149.00 | $299.00 | $300 | $399.00
USB - HS | N | N | N | N | Y | N | N | N | N
OS - Hardware | N | N | N | N | Y | N | N | N | N
OS - Firmware | N | Y | N | N | Y | Y | N | Y | N
OS - Driver | N | Y | N | N | Y | Y | N | Y | N
OS - API | N | Y | Y | N | Y | Y | Y | Y | N
ADC Channels | 8 | 8 | 16 | 8 | 15 | 8 | 14 | 8 | 8
ADC Bits | 10 | 12 | 12 | 12 | 12 | 12 | 16 | 16 | 12
DAC Channels | 0 | 0 | 2 | 2 | 5 | 2 | 2 | 1 | 2
DAC Bits | 0 | 0 | 12 | 12 | 12 | 12 | 12 | 14 | 12
GPIO | 4 | 8 | 16 | 24 | 60 | 8 | 20 | 6 | 16
SPI | 0 | 0 | 1 | 0 | 1 | 0 | 1 | 0 | 0
I2C | 0 | 0 | 1 | 0 | 2 | 0 | 1 | 0 | 0
CAN | 0 | 0 | 0 | 0 | 1 | 0 | 0 | 0 | 0
SDIO | 0 | 0 | 0 | 0 | 1 | 0 | 0 | 0 | 0

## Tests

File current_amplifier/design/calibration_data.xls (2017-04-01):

Calibration Data
Reference Voltage | 2.048 | Measured Value | 0.0128 | 12.8mV across the shunt resistor pads |  |  |  | Shunt Resistance = 12.8mV/250mA
Channel 1 offset | 0.01 | Error Value | 0.25 | 250mA test current |  |  |  | 0.0512
shunt resistance (nominal) = 51mOhm
Bias Voltage | 3
Board Number | 0mA |  |  |  |  |  | 10mA |  |  |  |  |  | 50mA |  |  |  |  |  | 100mA
 | V_20X (no offset) (V) | V_20X (corrected) | V_20X/(20*R) | V_FILT (V) | V_FILT/(96.8*R) | % Error V_FILT | V_20X (no offset) (V) | V_20X (corrected) | V_20X/(20*R) | V_FILT (V) | V_FILT/(96.8*R) | % Error V_FILT | V_20X (no offset) (V) | V_20X (corrected) | V_20X/(20*R) | V_FILT (V) | V_FILT/(96.8*R) | % Error V_FILT | V_20X (no offset) (V) | V_20X (corrected) | V_20X/(20*R) | V_FILT (V) | V_FILT/(96.8*R) | %Error V_FILT
1 | 2.056 | 2.0460 | -0.0020 | 2.064 | 0.0012 |  | 2.068 | 2.0580 | 0.0098 | 2.112 | 0.0109 | 8.96% | 2.106 | 2.096 | 0.0469 | 2.316 | 0.0521 | 4.11% | 2.16 | 2.1500 | 0.0996 | 2.568 | 0.1029 | 2.90%
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

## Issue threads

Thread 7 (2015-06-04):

marionette-daq/marionette-hardware #7: J7 should be a no place component

jalcok1, 2015-06-04:
If a user adds a shorting jumper across J7, 3.3V is shorted to ground and marionette reboots.  I believe the original intent was not to place this but we did not document it anywhere.  

If a user wants to provide a different Vref for the DAC they need to replace R18 with a different value, right now it is a 0 ohm resistor.

andrewgreenberg, 2015-06-04:
Hi!

Yes, that's probably a good idea. R18 and J7 should never be used at the
same time - you should desolder R18 and then add J7 to go to your own
custom vref. Hardly anyone will ever do this, so we don't need to
populate J7.

> If a user wants to provide a different Vref for the DAC they need to
> replace R18 with a different value, right now it is a 0 ohm resistor.

Again, they'll actually have to remove it.

Andrew

-- 
---------------------------------------------------------------------------
       Andrew Greenberg - andrew1602@gmail.com - 503.708.7711
---------------------------------------------------------------------------

andrewgreenberg, 2016-06-28:
Now is a no place component.

closed 2016-06-28 by andrewgreenberg

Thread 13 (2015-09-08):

marionette-daq/marionette-hardware #13: Resetting the external DAQ

kwilsonpdx, 2015-09-08:
### Found this note from the V2 Capstone guys. Do we want to implement a hardware reset?

* Maybe gate a GPIO with Board RESET_ and Supply...i dunno. More discussion needed?

*"If the dac124 chip has been configured and outputs have been written it will not reset if the marionette board is reset via software or the reset button. As it is powered by V CC , the registers on the dac124 will continue to output until it is reset or the board is removed from its power source. A possible fix to this would be to use a GPIO pin as the 3.3V power source so that when the board is reset and all pins are set to input floating the dac chip powers down."*

### Datasheet:
https://github.com/marionette-daq/marionette-hardware/blob/master/Datasheets/dac124s085.pdf

andrewgreenberg, 2015-09-08:
Oh hey, this is important. A user would expect a reset to reset EVERYTHING, most importantly any outputs. So let's do this. Except instead of powering the chip off the GPIO, just have it control a P-CH MOSFET to the analog supply.

andrewgreenberg, 2016-06-28:
Oh. Shit. Yeah, we forgot this on v2.1. WHY DOES NO READ THE ISSUES?! I keep telling... uh... telling myself.... uh... yeah.

Scheduling for v2.2... :/

andrewgreenberg, 2018-03-29:
Fixed! NRST is now hooked to V3.3DAC LDO's "EN" input. When NRST is pulled low, then v3.3DAC turns off, which power cycles and thus resets the DAC.

closed 2018-03-29 by andrewgreenberg

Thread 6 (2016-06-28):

### ISSUE TITLE
Silk screen for Analog Supply and DAC Supply is incorrectly labeled

### ISSUE THREAD

**Issue by jalcok1** [marionette-daq/marionette-hardware#6]
Both silkscreens indicate that one pin is vref_in when it is actually 3.3V.  The other pin says its 3.3V and it is actually vref_in.

**Comment by jalcok1** [comment]
Correction, the silk screen for the analog supply is the only one that is incorrect.

**Comment by jalcok1** [comment]
Even better ….. The silkscreen for DAC and Analog Vref should be just removed.  The connectors J7 and J4 don't really serve a purpose.

**Comment by andrewgreenberg** [comment]
Fixed in v2.

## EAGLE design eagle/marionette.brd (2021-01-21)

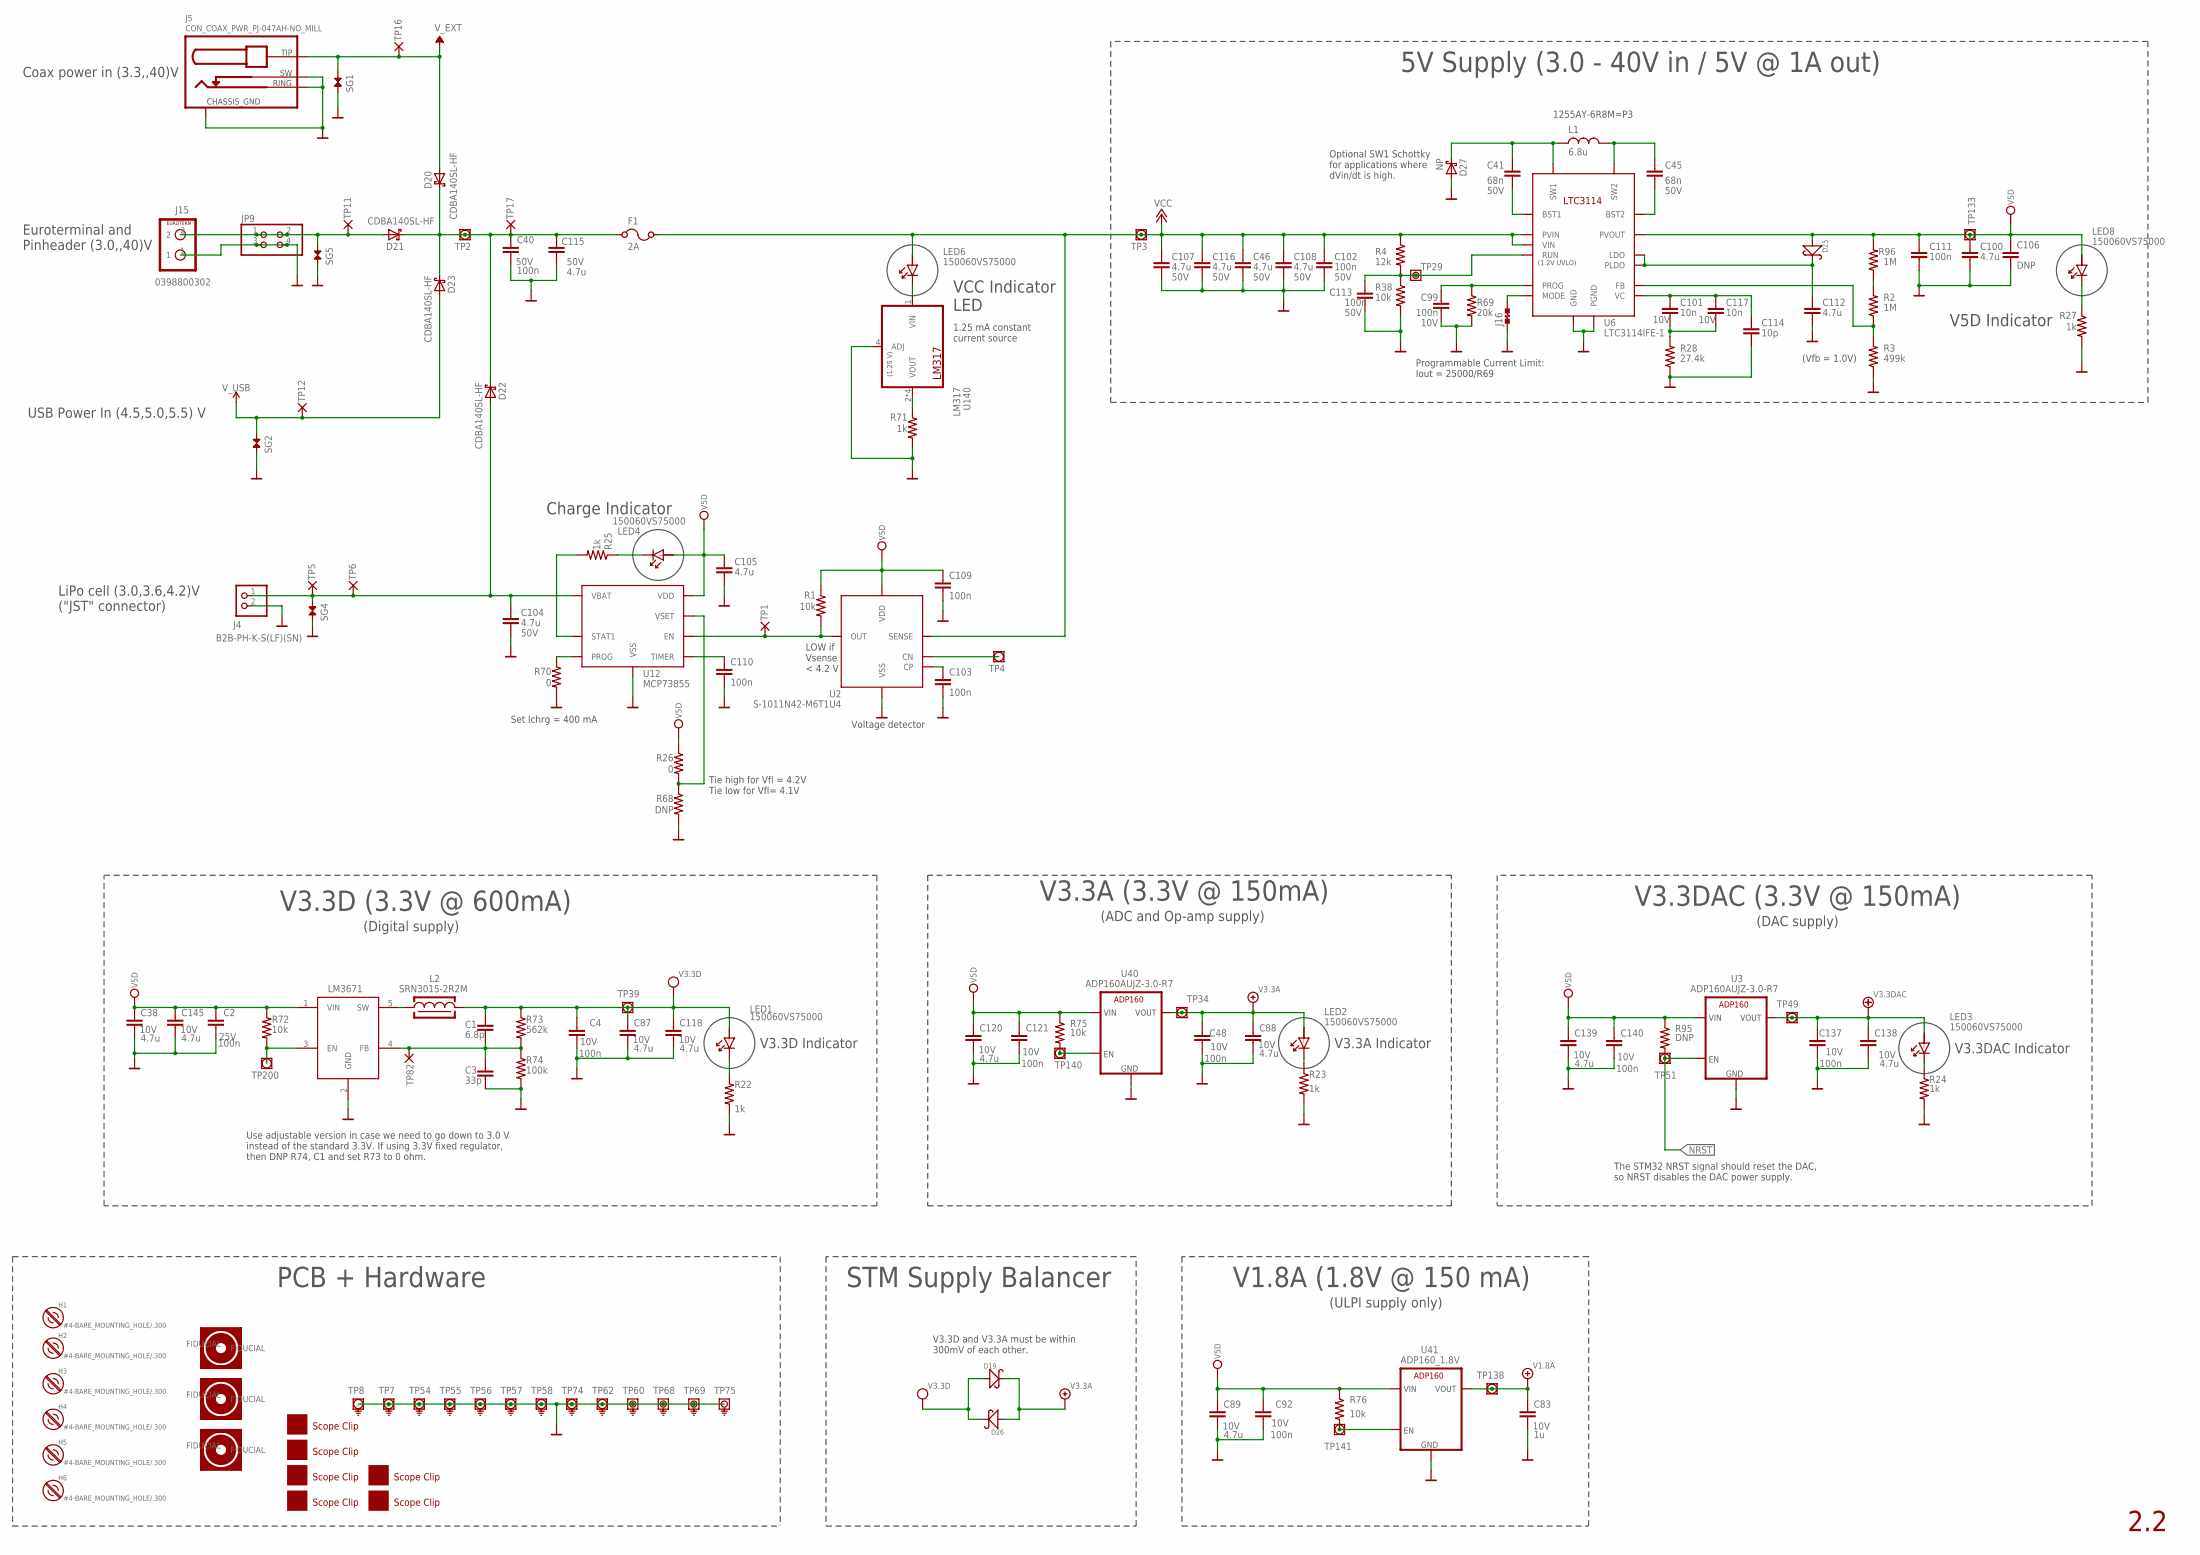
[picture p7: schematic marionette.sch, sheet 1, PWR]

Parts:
C1: 6.8p; .0402-B
C2, C4, C40, C48, C92, C99, C102, C103, C109, C110, C111, C113, C121, C137, C140: 100n; .0402-B
C3: 33p; .0402-B
C38, C46, C87, C88, C89, C100, C104, C105, C107, C108, C112, C115, C116, C118, C120, C138, C139, C145: 4.7u; .0805-B
C41, C45: 68n; .0402-B
C83: 1u; .0402-B
C101, C117: 10n; .0402-B
C106: DNP; 1206-B
C114: 10p; .0402-B
D19, D25, D26: VSKY05201006-G4-08; .0402-B-NOSILK-DIODE; MPN VSKY05201006-G4-08
D20, D21, D22, D23: CDBA140SL-HF; SMA
D27: NP; SMB
F1: 2A; R1206
FIDUCIAL2, FIDUCIAL3, FIDUCIAL6: FIDUCIAL-1.0X2.0
H1, H2, H3, H4, H5, H6: #4-BARE_MOUNTING_HOLE/.300; #4/.300-BARE+STD_NUT_OR_STAR_WASHER
J4: B2B-PH-K-S(LF)(SN); JST-PH-2-THM; MPN B2B-PH-K-S(LF)(SN)
J5: CON_COAX_PWR_PJ-047AH-NO_MILL; PJ-047_NO_MILLED_SLOTS
J15: 0398800302; CONN-TERM-EUROSTYLE_200MIL_2X1; MPN 0398800302
J16: JUMPER-SHORTED-CUTTABLE-E0402-0.3MM-NOSILK
J17, J18, J19, J20, J24, J25: SCOPE_CLIP_5MM_10MM
JP9: PINHD-2X2; 2X02
L1: 6.8u; L_SHIELDED_6.3MM_6.3MM_4.5MM
L2: SRN3015-2R2M; INDUCTOR_3MM_3MM_1.5MM
LED1, LED2, LED3, LED4, LED6, LED8: 150060VS75000; CHIPLED_0603
R1, R38, R72, R75, R76: 10k; .0402-B
R2, R96: 1M; .0402-B
R3: 499k; .0402-B
R4: 12k; .0402-B
R22, R23, R24, R25, R27, R71: 1k; .0402-B
R26, R70: 0; .0402-B
R28: 27.4k; .0402-B
R68, R95: DNP; .0402-B
R69: 20k; .0402-B
R73: 562k; .0402-B
R74: 100k; .0402-B
SG1, SG2, SG4, SG5: SPARKGAP_RECT_0.15MM; SPARKGAP_0.15MM
TP1, TP5, TP6, TP11, TP12, TP16, TP17: PAD+X-1.0-NO_CREAM+SILK; PAD-ROUND-1.0-NOCREAM+SILK
TP2, TP3, TP4, TP34, TP39, TP49, TP51, TP133, TP138, TP140, TP141, TP200: PAD+VIA_0.6MM
TP7, TP8, TP54, TP55, TP56, TP57, TP58, TP62, TP74: PAD+VIA_GND_0.6MM; PAD+GND_VIA_0.6MM
TP29: PAD+VIA_0.25MM
TP60, TP68, TP69, TP75: PAD+VIA_GND_0.25MM; PAD+GND_VIA_0.25MM
TP82: PAD+X-0.7-NO_CREAM+SILK; PAD-ROUND-0.7-NOCREAM+SILK
U2: S-1011N42-M6T1U4; SOT23-6; MPN S-1011N42-M6T1U4
U3, U40: ADP160AUJZ-3.0-R7; SOT23-5
U6: LTC3114IFE-1; 16-LEAD-PLASTIC-TSSOP-FE
U12: MCP73855; 10-LEAD-DFN
U17: LM3671; SOT23-5L
U41: ADP160_1.8V; SOT23-5
U140: LM317; SOIC-8

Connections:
BST1: C41.1, U6.13 (BST1)
BST2: C45.1, U6.12 (BST2)
CHG-ENABLE: R1.2, TP1.PAD, U2.3 (OUT), U12.10 (EN)
CHRG_IND_CATHODE: LED4.C, R25.1
CN: TP4.TP, U2.6 (CN)
CP: C103.1, U2.4 (CP)
GND: C2.1, C3.1, C4.1, C38.2, C40.2, C46.2, C48.1, C83.2, C87.2, C88.2, C89.2, C92.1, C99.1, C100.2, C102.1, C103.2, C104.2, C105.2, C106.2, C107.2, C108.2, C109.2, C110.2, C111.1, C112.2, C113.1, C114.1, C115.2, C116.2, C118.2, C120.2, C121.1, C137.1, C138.2, C139.2, C140.1, C145.2, D27.ANODE, J4.2 (1), J5.RING, J5.S1 (CHASSIS_GND), J5.S2 (CHASSIS_GND), J5.SWITCH (SW), J15.1, J16.1, JP9.3, JP9.4, R3.1, R22.2, R23.2, R24.2, R27.2, R28.1, R38.2, R68.2, R69.2, R70.2, R71.2, R74.2, SG1.2, SG2.2, SG4.2, SG5.2, TP7.TP, TP8.TP, TP54.TP, TP55.TP, TP56.TP, TP57.TP, TP58.TP, TP60.TP, TP62.TP, TP68.TP, TP69.TP, TP74.TP, TP75.TP, U2.5 (VSS), U3.2 (GND), U3.4 (GND), U6.1 (PGND), U6.8 (GND), U6.PAD (PGND), U12.4 (VSS), U12.7 (VSS), U12.EP (VSS), U17.2 (GND), U40.2 (GND), U40.4 (GND), U41.2 (GND), U41.4 (GND), U140.4 (ADJ); also elsewhere on the board
LED_CATH_V3.3A: LED2.C, R23.1
LED_CATH_V3.3D: LED1.C, R22.1
LED_CATH_V3.3DAC: LED3.C, R24.1
LM3671_EN: R72.2, TP200.TP, U17.3 (EN)
LM3671_FB: C1.1, C3.2, R73.2, R74.1, TP82.PAD, U17.4 (FB)
LM3671_SW: L2.2, U17.5 (SW)
LTC3114_FB: R2.1, R3.2, U6.7 (FB)
LTC3114_LDO: C112.1, D25.C (-), U6.9 (LDO), U6.11 (PLDO)
LTC3114_MODE: J16.2, U6.16 (MODE)
LTC3114_PROG: C99.2, R69.1, U6.5 (PROG)
LTC3114_RUN: C113.2, R4.2, R38.1, TP29.TP, U6.4 (RUN)
LTC3114_VC: C101.2, C114.2, C117.2, U6.6 (VC)
LTC3114_VC1: C101.1, C117.1, R28.2
MCP73855_PROG: R70.1, U12.5 (PROG)
MCP73855_STAT1: R25.2, U12.1 (STAT1)
MCP73855_VSET: R26.2, R68.1, U12.2 (VSET)
MIC5305_V1.8A_EN: R76.2, TP141.TP, U41.3 (EN)
MIC5305_V3.3_EN: R75.2, TP140.TP, U40.3 (EN)
NRST: R95.2, TP51.TP, U3.3 (EN); also elsewhere on the board
SW1: C41.2, D27.CATH (CATHODE), L1.1, U6.15 (SW1)
SW2: C45.2, L1.2, U6.2 (SW2)
TIMER: C110.1, U12.6 (TIMER)
V1.8A: C83.1, TP138.TP, U41.5 (VOUT); also elsewhere on the board
V3.3A: C48.2, C88.1, D19.C (-), D26.A (+), LED2.A, TP34.TP, U40.5 (VOUT); also elsewhere on the board
V3.3D: C1.2, C4.2, C87.1, C118.1, D19.A (+), D26.C (-), L2.1, LED1.A, R73.1, TP39.TP; also elsewhere on the board
V3.3DAC: C137.2, C138.1, LED3.A, TP49.TP, U3.5 (VOUT); also elsewhere on the board
V5D: C2.2, C38.1, C89.1, C92.2, C100.1, C105.1, C106.1, C109.1, C111.2, C120.1, C121.2, C139.1, C140.2, C145.1, D25.A (+), LED4.A, LED8.A, R1.1, R26.1, R72.1, R75.1, R76.1, R95.1, R96.2, TP133.TP, U2.1 (VDD), U3.1 (VIN), U6.3 (PVOUT), U12.3 (VDD), U17.1 (VIN), U40.1 (VIN), U41.1 (VIN); also elsewhere on the board
V5D_CATHODE: LED8.C, R27.1
V5D_FB_R: R2.2, R96.1
VBAT: C104.1, D22.A (ANODE), J4.1 (2), SG4.1, TP5.PAD, TP6.PAD, U12.8 (VBAT), U12.9 (VBAT)
VCC: C46.1, C102.2, C107.1, C108.1, C116.1, F1.2, LED6.A, R4.1, TP3.TP, U2.2 (SENSE), U6.10 (VIN), U6.14 (PVIN); also elsewhere on the board
VCC_CATHODE: LED6.C, U140.1 (VIN)
VCC_LED: R71.1, U140.2 (VOUT), U140.3 (VOUT), U140.6 (VOUT), U140.7 (VOUT)
VIN: C40.1, C115.1, D20.K (CATHODE), D21.K (CATHODE), D22.K (CATHODE), D23.K (CATHODE), F1.1, TP2.TP, TP17.PAD
VIN_EUROTERMINAL: D21.A (ANODE), J15.2, JP9.1, JP9.2, SG5.1, TP11.PAD
V_EXT: D20.A (ANODE), J5.TIP, SG1.1, TP16.PAD
V_USB: D23.A (ANODE), SG2.1, TP12.PAD; also elsewhere on the board

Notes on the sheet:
V3.3A (3.3V @ 150mA)
V1.8A (1.8V @ 150 mA)
PCB + Hardware
V3.3D (3.3V @ 600mA)
Coax power in (3.3,,40)V
Euroterminal and Pinheader (3.0,,40)V
USB Power In (4.5,5.0,5.5) V
V3.3DAC (3.3V @ 150mA)
V3.3D and V3.3A must be within 300mV of each other.
V5D Indicator
VCC Indicator LED
V3.3D Indicator
V3.3A Indicator
V3.3DAC Indicator
Use adjustable version in case we need to go down to 3.0 V instead of the standard 3.3V. If using 3.3V fixed regulator, then DNP R74, C1 and set R73 to 0 ohm.
5V Supply (3.0 - 40V in / 5V @ 1A out)
(ADC and Op-amp supply)
(DAC supply)
(Digital supply)
(ULPI supply only)
STM Supply Balancer
LiPo cell (3.0,3.6,4.2)V ("JST" connector)
Voltage detector
LOW if Vsense < 4.2 V
Charge Indicator
Tie high for Vfl = 4.2V Tie low for Vfl= 4.1V
Set Ichrg = 400 mA
1.25 mA constant current source
The STM32 NRST signal should reset the DAC, so NRST disables the DAC power supply.
(1.2V UVLO)
Programmable Current Limit: Iout = 25000/R69
(Vfb = 1.0V)
1255AY-6R8M=P3
Optional SW1 Schottky for applications where dVin/dt is high.

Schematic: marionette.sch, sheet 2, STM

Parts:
C5, C22, C26, C94, C96, C146, C153: 4.7u; .0805-B
C6, C27, C30: 10p; .0402-B
C7, C8, C9, C10, C11, C12, C13, C14, C15, C16, C17, C18, C19, C20, C21, C24, C25, C31, C36, C37, C39, C43, C44, C47, C86, C90, C91, C97, C98, C151, C152: 100n; .0402-B
C23, C28, C32, C85, C93: 1u; .0402-B
C29, C33, C142, C143: 10n; .0402-B
C34, C35: DNP; .0402-B
C42: 100p; .0402-B
D3: BAS40-00; SOT23-3
J2: PINHD-1X3; 1X03
J13: CONN_HEADER_JTAG; CONN_HEADER_JTAG_SMD_10PIN_50MIL
J14: CON_HIROSE_DM3D(MICROSD); HIROSE_DM3D(MICRO-SD)
J22: ZX62D-B-5P8
JP1: DNP; 1X02
JP2: PINHD-2X4; 2X04
LED5: SMLV56RGB1W1; LED-3528
Q3: AO3419; SOT23-3
R5, R8, R9, R10, R11, R67, R78: 47k; .0402-B
R6, R7, R202, R203: 4.7k; .0402-B
R12: 620; .0402-B
R13, R14: 510; .0402-B
R15, R16, R20, R37, R63, R64, R77: 10k; .0402-B
R17, R30, R66: 0; .0402-B
R18, R65, R108: 100k; .0402-B
R19, R105, R111: 1k; .0402-B
R29: 120; .0402-B
R104: 0; .0603-B
R201: 8.06k; .0402-B
R204: 1M; .0402-B
SB1, SB2, SB3: TRACE_BRIDGE_6MIL
SG3: SPARKGAP-5; SPARKGAP_5MIL
SW3, SW4: FSM1LPSTR; SWITCH_TAC_NO_GNDED
TCXO1: TCXO_D32G-026.0M; CRYSTAL-3.2X2.5(4_TERMINAL)
TP13, TP52, TP53: PAD+VIA_0.6MM
TP14, TP15, TP19, TP20, TP21, TP22, TP23, TP24, TP25, TP26, TP27, TP28, TP30, TP37, TP38, TP46, TP47, TP72, TP108, TP109: PAD+X-0.7-NO_CREAM+SILK; PAD-ROUND-0.7-NOCREAM+SILK
TP59: PAD+VIA_GND_0.6MM; PAD+GND_VIA_0.6MM
TP300, TP301: PAD+VIA_0.25MM
U1, U15: SWITCH_74HC4066D; SO14
U5: MAX3051ESAESA+; SO8
U11: STM32F427-STM32F427; LQFP176
U14: USB3320; QFN32-5X5
X1: ABSO7; 2-SMD_ABM7
XTAL1: DNP; CRYSTAL-3.2X2.5(4_TERMINAL)

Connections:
!ULPI_RST_B: R63.1, TP20.PAD, U11.162 (PB4), U14.27 (!RST_B)
ADC2_CH2_FLT: U11.42 (PA2); also elsewhere on the board
ADC2_CH6_FLT: U11.52 (PA6); also elsewhere on the board
ADC2_CH7_FLT: U11.53 (PA7); also elsewhere on the board
ADC2_CH11_FLT: U11.33 (PC1); also elsewhere on the board
ADC2_CH13_FLT: U11.35 (PC3); also elsewhere on the board
ADC2_CH14_FLT: U11.54 (PC4); also elsewhere on the board
ADC2_CH15_FLT: U11.55 (PC5); also elsewhere on the board
ADC3_CH5_FLT: U11.25 (PF7); also elsewhere on the board
ADC3_CH6_FLT: U11.26 (PF8); also elsewhere on the board
ADC3_CH7_FLT: U11.27 (PF9); also elsewhere on the board
ADC3_CH8_FLT: U11.28 (PF10); also elsewhere on the board
ADC3_CH9_FLT: U11.19 (PF3); also elsewhere on the board
ADC3_CH14_FLT: U11.20 (PF4); also elsewhere on the board
ADC3_CH15_FLT: U11.21 (PF5); also elsewhere on the board
BOOT0: JP2.3, JP2.4, R37.2, SW4.1, SW4.2 (P1), TP26.PAD, U11.166 (BOOT0)
BOOT1: R64.2, TP300.TP, U11.58 (PB2)
CAN1-H: R29.2, U5.7 (CANH); also elsewhere on the board
CAN1-L: R29.1, U5.6 (CANL); also elsewhere on the board
CAN_RS: R30.2, U5.8 (RS)
DM: J22.P2 (D-), U14.19 (DM/DP)
DP: J22.P3 (D+), R104.2
DP_1: R104.1, U14.18 (DP/DM)
GND: C5.2, C6.1, C7.2, C8.2, C9.2, C10.2, C11.2, C12.2, C13.2, C14.2, C15.2, C16.2, C17.2, C18.2, C19.2, C20.2, C21.2, C22.2, C23.2, C24.2, C25.2, C26.2, C27.2, C28.2, C29.2, C30.1, C31.2, C32.2, C33.2, C34.2, C35.2, C36.2, C37.2, C39.2, C43.2, C44.1, C47.2, C85.2, C86.2, C91.2, C93.2, C94.2, C96.2, C97.2, C142.2, C143.2, C146.2, C151.2, C152.2, C153.2, J2.3, J13.3, J13.5, J13.9, J14.G1 (PAD), J14.G2 (PAD), J14.G3 (PAD), J14.G4 (PAD), J14.P6 (6), J14.S1 (1), J22.P5 (GND), JP1.2, JP2.7, JP2.8, R18.1, R30.1, R37.1, R63.2, R64.1, R67.1, R108.2, R201.2, R204.2, SB1.1, SG3.2, SW3.3 (P2), SW3.4 (P2), SW3.5 (SHIELD_PIN), SW4.5 (SHIELD_PIN), TCXO1.2 (GND), TP59.TP, U1.7 (V-), U5.2 (GND), U11.14 (VSS), U11.22 (VSS), U11.37 (VSSA), U11.48 (BYPASS_REG), U11.61 (VSS), U11.71 (VSS), U11.90 (VSS), U11.102 (VSS), U11.113 (VSS), U11.126 (VSS), U11.135 (VSS), U11.148 (VSS), U11.158 (VSS), U14.PAD (GND), U15.6 (EN), U15.7 (V-), U15.8 (Y), U15.9 (Z), U15.10 (Z), U15.11 (Y), U15.12 (EN), XTAL1.2 (GND), XTAL1.4 (GND); also elsewhere on the board
LED_STATUS_B_CATH: LED5.6 (K), R14.2
LED_STATUS_G_CATH: LED5.4 (K), R13.2
LED_STATUS_R_CATH: LED5.5 (K), R12.2
MBUS_ANALOG_SCL: U1.2 (Z); also elsewhere on the board
MBUS_ANALOG_SDA: U1.3 (Z); also elsewhere on the board
MBUS_GPIO_SCL: U15.2 (Z); also elsewhere on the board
MBUS_GPIO_SDA: U15.3 (Z); also elsewhere on the board
MBUS_SERIAL_SCL: U1.9 (Z); also elsewhere on the board
MBUS_SERIAL_SDA: U1.10 (Z); also elsewhere on the board
MCO1: C98.1, TP301.TP, U11.119 (PA8)
NRST: C31.1, J13.10, JP2.5, JP2.6, R16.1, R111.2, SW3.1, SW3.2 (P1), TP24.PAD; also elsewhere on the board
NRST_FILTERED: R111.1, U11.31 (NRST)
OSC32_IN: C27.1, TP38.PAD, U11.9 (PC14), X1.P$1
OSC32_OUT: C30.2, TP37.PAD, U11.10 (PC15), X1.P$2
OSC_IN: C35.1, C90.1, R18.2, U11.29 (PH0), XTAL1.3 (2)
OSC_OUT: C34.1, TP30.PAD, U11.30 (PH1), XTAL1.1
PA0_UART4_TX: U11.40 (PA0); also elsewhere on the board
PA1_UART4_RX: U11.41 (PA1); also elsewhere on the board
PA10_SDIO_PWR: R20.2, U11.121 (PA10)
PA11_USB_FS_N: TP23.PAD, U11.122 (PA11), U14.15 (SPK_L)
PA12_USB_FS_P: TP22.PAD, U11.123 (PA12), U14.16 (SPK_R)
PA15_TIM2_CH1_ETR: U11.138 (PA15); also elsewhere on the board
PB6_I2C1_SCL: R6.1, TP52.TP, U1.1 (Y), U1.8 (Y), U11.164 (PB6), U15.1 (Y)
PB7_I2C1_SDA: R7.1, TP53.TP, U1.4 (Y), U1.11 (Y), U11.165 (PB7), U15.4 (Y)
PB8_TIM4_CH3: U11.167 (PB8); also elsewhere on the board
PB9_TIM4_CH4: U11.168 (PB9); also elsewhere on the board
PB14: U11.94 (PB14); also elsewhere on the board
PB15: U11.95 (PB15); also elsewhere on the board
PC6_DEBUG_USART6_TX: J2.1, U11.115 (PC6)
PC7_DEBUG_USART6_RX: J2.2, U11.116 (PC7)
PC8_SDIO_D0: J14.P7 (7), R8.1, TP28.PAD, U11.117 (PC8)
PC9_SDIO_D1: J14.P8 (8), R11.1, U11.118 (PC9)
PC10_SDIO_D2: J14.P1 (1), R78.1, U11.139 (PC10)
PC11_SDIO_D3: J14.P2 (2), R10.1, U11.140 (PC11)
PC12_SDIO_CK: J14.P5 (5), U11.141 (PC12)
PC13: U11.8 (PC13); also elsewhere on the board
PD0: U11.142 (PD0); also elsewhere on the board
PD1: U11.143 (PD1); also elsewhere on the board
PD2_SDIO_CMD: J14.P3 (3), R9.1, U11.144 (PD2)
PD3_USART2_CTS: U11.145 (PD3); also elsewhere on the board
PD4_USART2_RTS: U11.146 (PD4); also elsewhere on the board
PD5_USART2_TX: U11.147 (PD5); also elsewhere on the board
PD6_USART2_RX: U11.150 (PD6); also elsewhere on the board
PD7: U11.151 (PD7); also elsewhere on the board
PD8_USART3_TX: U11.96 (PD8); also elsewhere on the board
PD9_USART3_RX: U11.97 (PD9); also elsewhere on the board
PD10_SD_DETECT: J14.S0 (0), U11.98 (PD10)
PD11_USART3_CTS: U11.99 (PD11); also elsewhere on the board
PD12_USART3_RTS: U11.100 (PD12); also elsewhere on the board
PD13_LED_STATUS_R: R12.1, U11.101 (PD13)
PD14_LED_STATUS_G: R13.1, U11.104 (PD14)
PD15_LED_STATUS_B: R14.1, U11.105 (PD15)
PE0_TIM4_ETR: U11.169 (PE0); also elsewhere on the board
PE1: U11.170 (PE1); also elsewhere on the board
PE2: U11.1 (PE2); also elsewhere on the board
PE3: U11.2 (PE3); also elsewhere on the board
PE4: U11.3 (PE4)
PE5_TIM9_CH1: U11.4 (PE5); also elsewhere on the board
PE6_TIM9_CH2: U11.5 (PE6); also elsewhere on the board
PE7_TIM1_ETR: U11.68 (PE7); also elsewhere on the board
PE8: U11.69 (PE8); also elsewhere on the board
PE9_TIM1_CH1: U11.70 (PE9); also elsewhere on the board
PE10: U11.73 (PE10)
PE11_DAC_SPI4_NSS: U11.74 (PE11); also elsewhere on the board
PE12_DAC_SPI4_SCK: U11.75 (PE12); also elsewhere on the board
PE13_TIM1_CH3: U11.76 (PE13); also elsewhere on the board
PE14_DAC_SPI4_MOSI: U11.77 (PE14); also elsewhere on the board
PE15: U11.78 (PE15)
PF0_I2C2_SDA: R202.1, TP47.PAD, U11.16 (PF0); also elsewhere on the board
PF1_I2C2_SCL: R203.1, TP46.PAD, U11.17 (PF1); also elsewhere on the board
PF2_CAN_SHDN: R77.1, TP72.PAD, U5.5 (SHDN), U11.18 (PF2)
PF6: U11.24 (PF6)
PF11: U11.59 (PF11); also elsewhere on the board
PF12: U11.60 (PF12); also elsewhere on the board
PF13: U11.63 (PF13); also elsewhere on the board
PF14: U11.64 (PF14); also elsewhere on the board
PF15: U11.65 (PF15); also elsewhere on the board
PG0: U11.66 (PG0); also elsewhere on the board
PG1: U11.67 (PG1); also elsewhere on the board
PG2: U11.106 (PG2); also elsewhere on the board
PG3: U11.107 (PG3); also elsewhere on the board
PG4: U11.108 (PG4); also elsewhere on the board
PG5: U11.109 (PG5); also elsewhere on the board
PG6: U11.110 (PG6); also elsewhere on the board
PG7: U11.111 (PG7); also elsewhere on the board
PG8_SPI6_NSS: U11.112 (PG8); also elsewhere on the board
PG9: U11.152 (PG9); also elsewhere on the board
PG10: U11.153 (PG10); also elsewhere on the board
PG11: U11.154 (PG11); also elsewhere on the board
PG12_SPI6_MISO: U11.155 (PG12); also elsewhere on the board
PG13_SPI6_SCK: U11.156 (PG13); also elsewhere on the board
PG14_SPI6_MOSI: U11.157 (PG14); also elsewhere on the board
PG15: U11.160 (PG15); also elsewhere on the board
PH2: U11.43 (PH2); also elsewhere on the board
PH3: U11.44 (PH3); also elsewhere on the board
PH5: U11.46 (PH5); also elsewhere on the board
PH6: U11.83 (PH6); also elsewhere on the board
PH7_ADC3_CH4: R6.2, U11.84 (PH7)
PH8_ADC3_CH8: R7.2, U11.85 (PH8)
PH9: U11.86 (PH9); also elsewhere on the board
PH10_TIM5_CH1: U11.87 (PH10); also elsewhere on the board
PH11_TIM5_CH2: U11.88 (PH11); also elsewhere on the board
PH12_TIM5_CH3: U11.89 (PH12); also elsewhere on the board
PH13_CAN1_TX: U5.1 (TXD), U11.128 (PH13)
PH14: U11.129 (PH14); also elsewhere on the board
PH15: U11.130 (PH15); also elsewhere on the board
PI0_SPI2_NSS: U11.131 (PI0); also elsewhere on the board
PI1_SPI2_SCK: U11.132 (PI1); also elsewhere on the board
PI2_SPI2_MISO: U11.133 (PI2); also elsewhere on the board
PI3_SPI2_MOSI: U11.134 (PI3); also elsewhere on the board
PI4: U11.173 (PI4); also elsewhere on the board
PI5_MBUS_ANA_SELECT: U1.5 (EN), U1.13 (EN), U11.174 (PI5)
PI6_MBUS_SER_SELECT: U1.6 (EN), U1.12 (EN), U11.175 (PI6)
PI7_MBUS_GPIO_SELECT: U11.176 (PI7), U15.5 (EN), U15.13 (EN)
PI8: U11.7 (PI8); also elsewhere on the board
PI9_CAN1_RX: U5.4 (RXD), U11.11 (PI9)
PI10: U11.12 (PI10); also elsewhere on the board
PI11: U11.13 (PI11); also elsewhere on the board
RBIAS: R201.1, TP21.PAD, U14.24 (RBIAS)
REFSEL_0: SB1.2, U14.8 (S0)
REFSEL_1: SB2.2, U14.11 (S1)
REFSEL_2: SB3.2, U14.14 (S2)
SDIO-PWR-SWITCHED: C42.1, C43.1, C96.1, C146.1, J14.P4 (4), Q3.3 (D), R108.1, TP15.PAD
SDIO-PWR_GATE: C42.2, Q3.1 (G), R20.1, R65.2, TP27.PAD
SHLD: C36.1, J22.P$1 (SHLD), J22.P$2 (SHLD), J22.P$3 (SHLD), J22.P$4 (SHLD), R204.1, SG3.1
STM-VBAT: D3.3 (CATHODE), TP13.TP, U11.6 (VBAT)
STM-VREF+: C23.1, C24.1, C143.1, JP1.1, R66.1, TP14.PAD, U11.38 (VREF+)
STM_DAC: U11.50 (PA4); also elsewhere on the board
STM_VCAP_1: C5.1, C37.1, U11.81 (VCAP_1)
STM_VCAP_2: C94.1, C97.1, U11.125 (VCAP_2)
SWDCK: J13.4, U11.137 (PA14)
SWDIO: J13.2, U11.124 (PA13)
SWO: J13.6, U11.161 (PB3)
TCXO_OUT: R17.1, TCXO1.3 (OUT)
TCXO_RC: C6.2, C90.2, R17.2
ULPI_CK: U11.51 (PA5), U14.1 (CLK)
ULPI_D0: U11.47 (PA3), U14.3 (D0)
ULPI_D1: U11.56 (PB0), U14.4 (D1)
ULPI_D2: U11.57 (PB1), U14.5 (D2)
ULPI_D3: U11.79 (PB10), U14.6 (D3)
ULPI_D4: U11.80 (PB11), U14.7 (D4)
ULPI_D5: U11.92 (PB12), U14.9 (D5)
ULPI_D6: U11.93 (PB13), U14.10 (D6)
ULPI_D7: U11.163 (PB5), U14.13 (D7)
ULPI_DIR: U11.34 (PC2), U14.31 (DIR)
ULPI_NXT: U11.45 (PH4), U14.2 (NXT)
ULPI_STP: U11.32 (PC0), U14.29 (STP)
USB3320_CPEN: TP108.PAD, U14.17 (CPEN)
USB3320_VBUS: R15.2, U14.22 (VBUS)
USB3320_XIN: C98.2, R5.1, R67.2, U14.26 (XI)
USB3320_XOUT: TP109.PAD, U14.25 (XO)
USB_ID: J22.P4 (ID), U14.23 (ID)
V1.8A: C29.1, C85.1, R5.2, U14.28 (1.8V), U14.30 (1.8V); also elsewhere on the board
V3.3A: C25.1, C26.1, C142.1, R66.2, U11.39 (VDDA); also elsewhere on the board
V3.3D: C7.1, C8.1, C9.1, C10.1, C11.1, C12.1, C13.1, C14.1, C15.1, C16.1, C17.1, C18.1, C19.1, C20.1, C21.1, C22.1, C28.1, C33.1, C44.2, C47.1, C86.1, C93.1, C151.1, C153.1, J13.1, JP2.1, JP2.2, LED5.1 (A), LED5.2 (A), LED5.3 (A), Q3.2 (S), R8.2, R9.2, R10.2, R11.2, R16.2, R19.2, R65.1, R77.2, R78.2, R202.2, R203.2, SB2.1, SB3.1, SW4.3 (P2), SW4.4 (P2), TCXO1.4 (VCC), TP25.PAD, U5.3 (VCC), U11.15 (VDD), U11.23 (VDD), U11.36 (VDD), U11.49 (VDD), U11.62 (VDD), U11.72 (VDD), U11.82 (VDD), U11.91 (VDD), U11.103 (VDD), U11.114 (VDD), U11.127 (VDD), U11.136 (VDD), U11.149 (VDD), U11.159 (VDD), U11.171 (PDR_ON), U11.172 (VDD), U14.20 (3.3V), U14.21 (VBAT), U14.32 (VIO); also elsewhere on the board
V5D: C39.1, C91.1, U1.14 (V+), U15.14 (V+); also elsewhere on the board
VBAT_ANODE: D3.1 (ANODE), R19.1
VBUS_FILTERED: R105.2, U11.120 (PA9)
V_USB: C32.1, C152.1, J22.P1 (VCC), R15.1, R105.1, TP19.PAD; also elsewhere on the board

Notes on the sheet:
2mA
32.768kHz CLK
USB HS PHY
SD Card Interface
*See Figure 8-1 USB3320 data sheet for application diagram
*Verify Rvbus value table 5-7 of USB3320 data sheet
STM CONTROL
KEY
SWD Interface
*RS pulled low for HS operation value of RS resistor controls output slope.
26 MHz XTAL / TCXO (choose one/ see IMPORTANT note)
CAN Transceiver
Analog Connector ID
Serial Connector ID
GPIO Connector ID
Marionette Bus Connector ID
Each 40 pin connector has two "MBUS ID" pins which can identify the system plugged into the connector. MBUS ID can either be two analog levels (resistive voltage dividers) or an MBUS-approved I2C memory.
To use the analog mode of the MBUS ID pins: 1 - Tri-state the I2C port pins PB6 and PB7 2 - Choose the right MBUS port switch (PI5, PI6, PI7) 3 - Sample the voltage on the two pins with the ADC.
In the TCXO circuit option: Rseries is for gain control. Rshunt is specified in datasheet for proper operation of TCXO. Cseries is for DC blocking. Cpar is to low pass filter square wave. Also, the values of the components in this block are given as XTAL/TCXO which give a value for each populating 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
26.00000MHz @ 10ppm
Unused gates connected to GND
STM32 VDD Bypass
STM Power
USB Micro B Connector
Connor-Winfield D32G-026.0M 26MHz TCXO requires supply voltage of (3.135V, 3.300V, 3.456V)
R104 is an 0603 jumper to swap DM/DP pins, rather than switching bit in USB3320 Register.
To use the I2C mode of the BMUS ID pins: 1 - Set PH7 and PH8 to GPIO pins and set them high, turning on the pull-up resistors. 2 - Use I2C1 to look for MBUS-approved memory ICs.
/3.1G
/4.5J
/4.5M
100k Pulldown resistor ensures SD card will power down quickly.
STM32
ABS07 32.768kHz crystal has load capacitance of 12.5pF. The trace capacitance is about 1pF. Therefore choose parallel caps of 11pF.
The 26 MHz XTAL, Connor Winfield MPN: 403C11A26M00000 has a load capacitance of 10 pF. The traces are relatively short, therefore use 10 pF bypass caps for C34 and C35.
Active High (high closes switch)
DEBUG UART TX
To I2C pins
To ADC Pins / GPIO high output for 4.7k I2C resistors
and PH7_ADC3_CH4 via R6 (4.7k)
and PH8_ADC3_CH8 via R7 (4.7k)

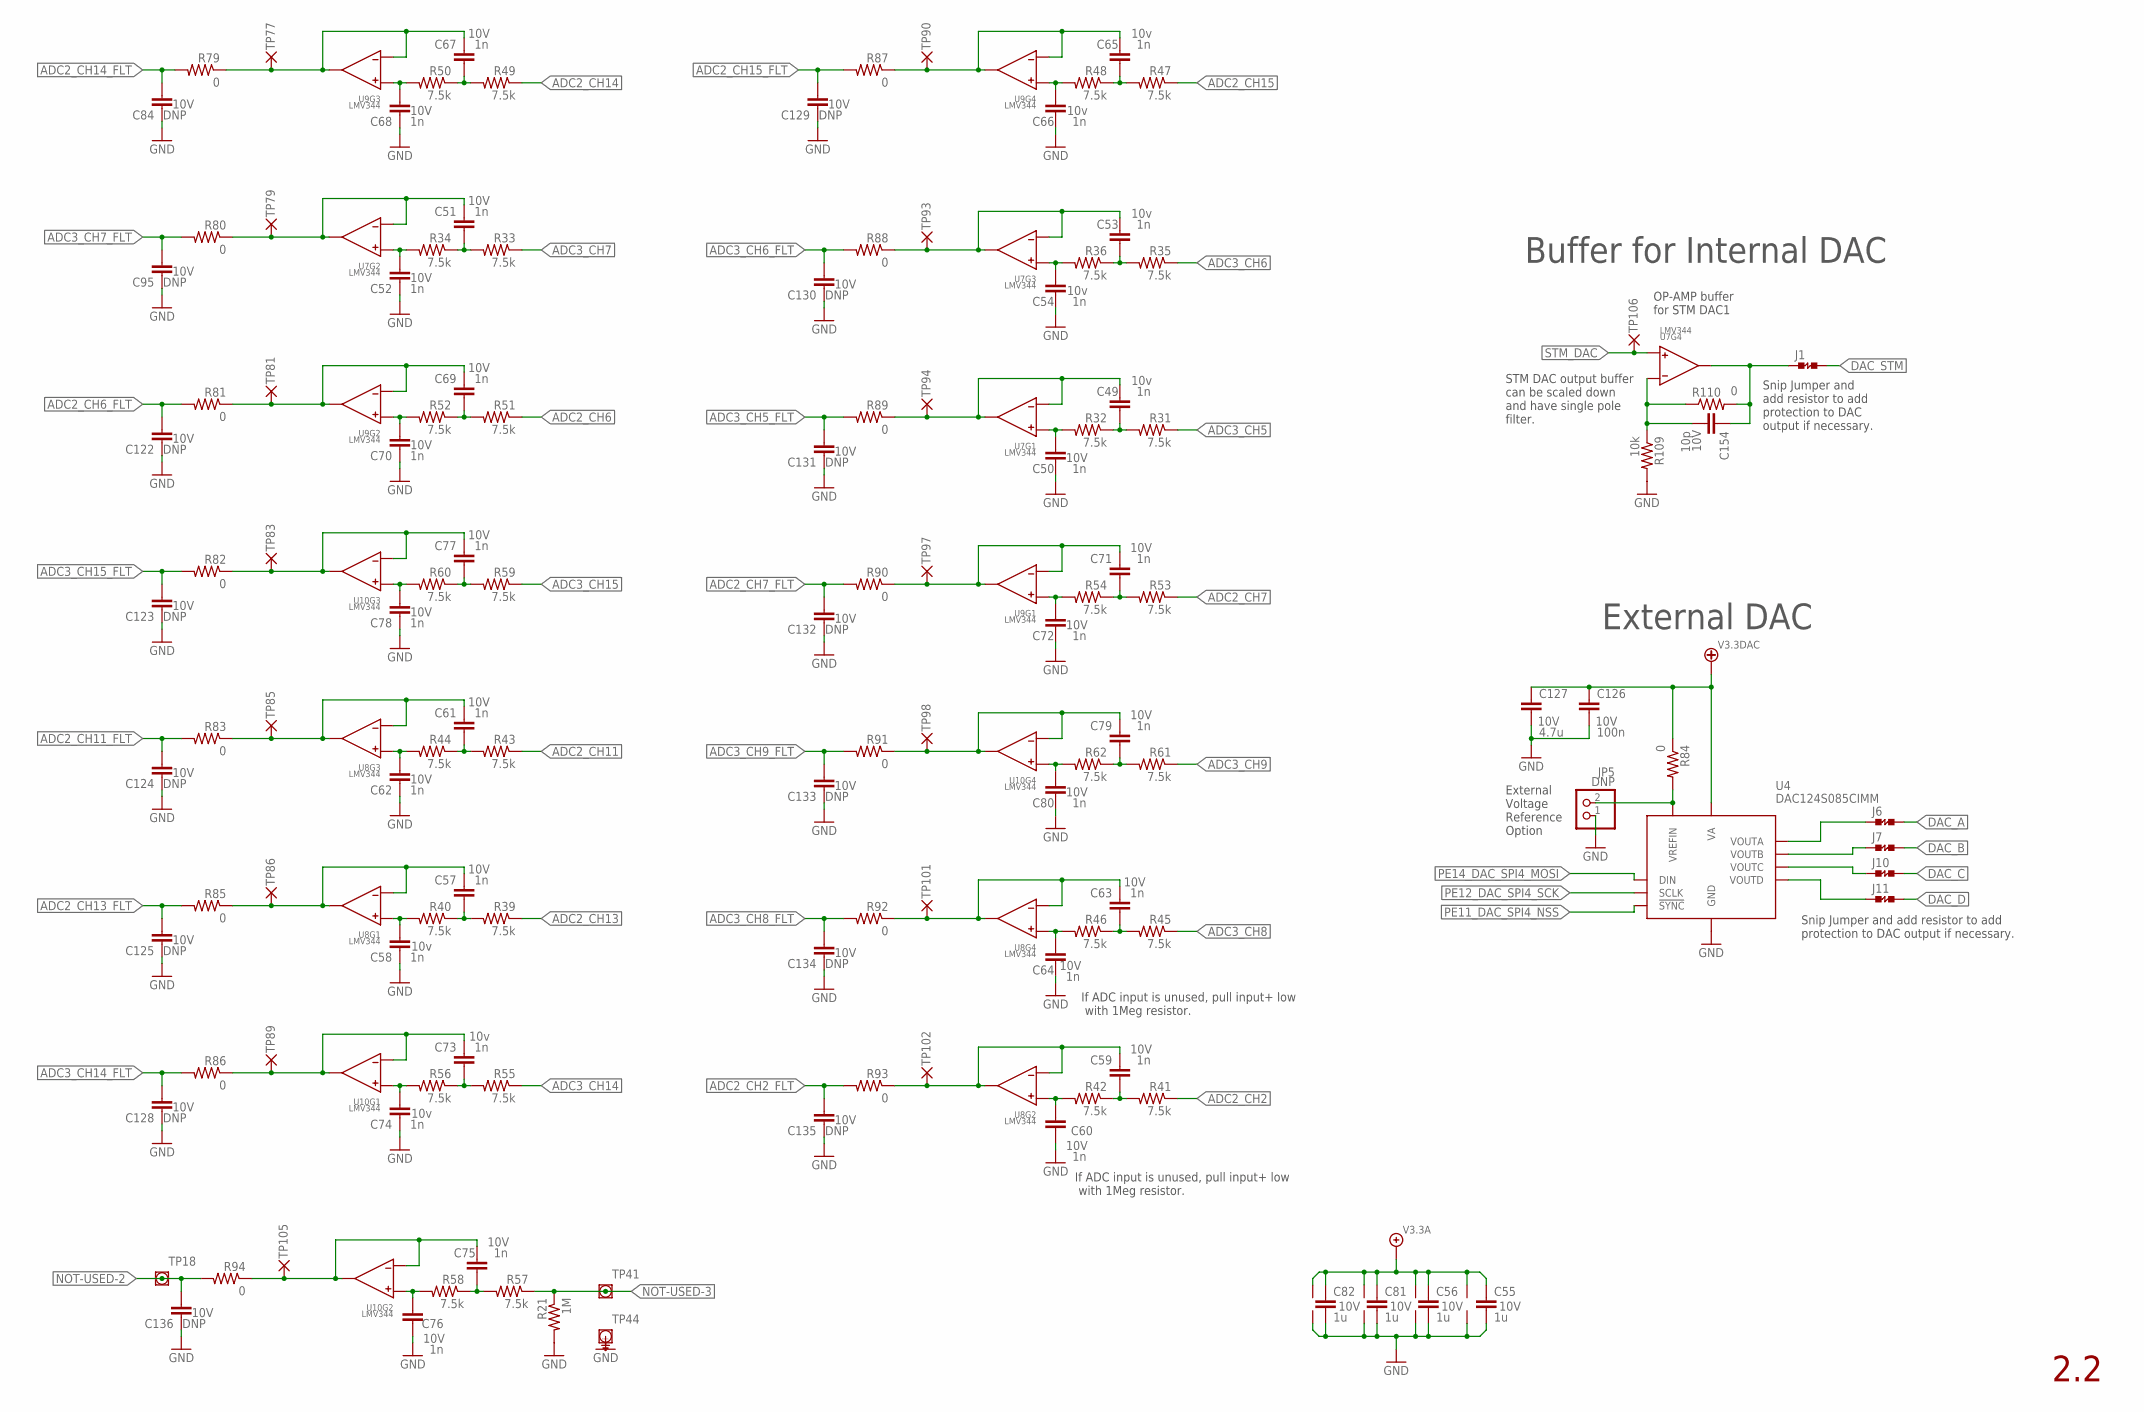
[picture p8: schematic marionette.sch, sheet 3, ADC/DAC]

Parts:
C49, C50, C51, C52, C53, C54, C57, C58, C59, C60, C61, C62, C63, C64, C65, C66, C67, C68, C69, C70, C71, C72, C73, C74, C75, C76, C77, C78, C79, C80: 1n; .0402-B
C55, C56, C81, C82: 1u; .0402-B
C84, C95, C122, C123, C124, C125, C128, C129, C130, C131, C132, C133, C134, C135, C136: DNP; .0402-B
C126: 100n; .0402-B
C127: 4.7u; .0805-B
C154: 10p; .0402-B
J1, J6, J7, J10, J11: JUMPER-SHORTED-CUTTABLE-E0402-0.3MM
JP5: DNP; 1X02
R21: 1M; .0402-B
R31, R32, R33, R34, R35, R36, R39, R40, R41, R42, R43, R44, R45, R46, R47, R48, R49, R50, R51, R52, R53, R54, R55, R56, R57, R58, R59, R60, R61, R62: 7.5k; .0402-B
R79, R80, R81, R82, R83, R84, R85, R86, R87, R88, R89, R90, R91, R92, R93, R94, R110: 0; .0402-B
R109: 10k; .0402-B
TP18, TP41: PAD+VIA_0.6MM
TP44: PAD+VIA_GND_0.6MM; PAD+GND_VIA_0.6MM
TP77, TP79, TP81, TP83, TP85, TP86, TP89, TP90, TP93, TP94, TP97, TP98, TP101, TP102, TP105, TP106: PAD+X-0.7-NO_CREAM+SILK; PAD-ROUND-0.7-NOCREAM+SILK
U4: DAC124S085CIMM; 10-TFSOP
U7, U8, U9, U10: LMV344; SOIC-14

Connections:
ADC1/2/3_CH2_OUT: C59.1, R93.1, TP102.PAD, U8.6 (-V), U8.7 (OUT)
ADC1/2/3_CH11_OUT: C61.1, R83.1, TP85.PAD, U8.8 (OUT), U8.9 (-V)
ADC1/2/3_CH13_OUT: C57.1, R85.1, TP86.PAD, U8.1 (OUT), U8.2 (-V)
ADC1/2/3_IN2+: C60.1, R42.2, U8.5 (+V)
ADC1/2/3_IN2_FILT: C59.2, R41.2, R42.1
ADC1/2/3_IN11+: C62.1, R44.2, U8.10 (+V)
ADC1/2/3_IN11_FILT: C61.2, R43.2, R44.1
ADC1/2/3_IN13+: C58.1, R40.2, U8.3 (+V)
ADC1/2/3_IN13_FILT: C57.2, R39.2, R40.1
ADC1/2_CH6_OUT: C69.1, R81.1, TP81.PAD, U9.6 (-V), U9.7 (OUT)
ADC1/2_CH7_OUT: C71.1, R90.1, TP97.PAD, U9.1 (OUT), U9.2 (-V)
ADC1/2_CH14_OUT: C67.1, R79.1, TP77.PAD, U9.8 (OUT), U9.9 (-V)
ADC1/2_CH15_OUT: C65.1, R87.1, TP90.PAD, U9.13 (-V), U9.14 (OUT)
ADC1/2_IN6+: C70.1, R52.2, U9.5 (+V)
ADC1/2_IN6_FILT: C69.2, R51.2, R52.1
ADC1/2_IN7+: C72.1, R54.2, U9.3 (+V)
ADC1/2_IN7_FILT: C71.2, R53.2, R54.1
ADC1/2_IN14+: C68.1, R50.2, U9.10 (+V)
ADC1/2_IN14_FILT: C67.2, R49.2, R50.1
ADC1/2_IN15+: C66.1, R48.2, U9.12 (+V)
ADC1/2_IN15_FILT: C65.2, R47.2, R48.1
ADC2_CH2: R41.1; also elsewhere on the board
ADC2_CH2_FLT: C135.1, R93.2; also elsewhere on the board
ADC2_CH6: R51.1; also elsewhere on the board
ADC2_CH6_FLT: C122.1, R81.2; also elsewhere on the board
ADC2_CH7: R53.1; also elsewhere on the board
ADC2_CH7_FLT: C132.1, R90.2; also elsewhere on the board
ADC2_CH11: R43.1; also elsewhere on the board
ADC2_CH11_FLT: C124.1, R83.2; also elsewhere on the board
ADC2_CH13: R39.1; also elsewhere on the board
ADC2_CH13_FLT: C125.1, R85.2; also elsewhere on the board
ADC2_CH14: R49.1; also elsewhere on the board
ADC2_CH14_FLT: C84.1, R79.2; also elsewhere on the board
ADC2_CH15: R47.1; also elsewhere on the board
ADC2_CH15_FLT: C129.1, R87.2; also elsewhere on the board
ADC3_CH4_OUT: C75.1, R94.1, TP105.PAD, U10.6 (-V), U10.7 (OUT)
ADC3_CH5: R31.1; also elsewhere on the board
ADC3_CH5_FLT: C131.1, R89.2; also elsewhere on the board
ADC3_CH5_OUT: C49.1, R89.1, TP94.PAD, U7.1 (OUT), U7.2 (-V)
ADC3_CH6: R35.1; also elsewhere on the board
ADC3_CH6_FLT: C130.1, R88.2; also elsewhere on the board
ADC3_CH6_OUT: C53.1, R88.1, TP93.PAD, U7.8 (OUT), U7.9 (-V)
ADC3_CH7: R33.1; also elsewhere on the board
ADC3_CH7_FLT: C95.1, R80.2; also elsewhere on the board
ADC3_CH7_OUT: C51.1, R80.1, TP79.PAD, U7.6 (-V), U7.7 (OUT)
ADC3_CH8: R45.1; also elsewhere on the board
ADC3_CH8_FLT: C134.1, R92.2; also elsewhere on the board
ADC3_CH8_OUT: C63.1, R92.1, TP101.PAD, U8.13 (-V), U8.14 (OUT)
ADC3_CH9: R61.1; also elsewhere on the board
ADC3_CH9_FLT: C133.1, R91.2; also elsewhere on the board
ADC3_CH14: R55.1; also elsewhere on the board
ADC3_CH14_FLT: C128.1, R86.2; also elsewhere on the board
ADC3_CH14_OUT: C73.1, R86.1, TP89.PAD, U10.1 (OUT), U10.2 (-V)
ADC3_CH15: R59.1; also elsewhere on the board
ADC3_CH15_FLT: C123.1, R82.2; also elsewhere on the board
ADC3_CH15_OUT: C77.1, R82.1, TP83.PAD, U10.8 (OUT), U10.9 (-V)
ADC3_IN4+: C76.1, R58.2, U10.5 (+V)
ADC3_IN4_FILT: C75.2, R57.2, R58.1
ADC3_IN5+: C50.1, R32.2, U7.3 (+V)
ADC3_IN5_FILT: C49.2, R31.2, R32.1
ADC3_IN6+: C54.1, R36.2, U7.10 (+V)
ADC3_IN6_FILT: C53.2, R35.2, R36.1
ADC3_IN7+: C52.1, R34.2, U7.5 (+V)
ADC3_IN7_FILT: C51.2, R33.2, R34.1
ADC3_IN8+: C64.1, R46.2, U8.12 (+V)
ADC3_IN8_FILT: C63.2, R45.2, R46.1
ADC3_IN9+: C80.1, R62.2, U10.12 (+V)
ADC3_IN9_FILT: C79.2, R61.2, R62.1
ADC3_IN9_OUT: C79.1, R91.1, TP98.PAD, U10.13 (-V), U10.14 (OUT)
ADC3_IN14+: C74.1, R56.2, U10.3 (+V)
ADC3_IN14_FILT: C73.2, R55.2, R56.1
ADC3_IN15+: C78.1, R60.2, U10.10 (+V)
ADC3_IN15_FILT: C77.2, R59.2, R60.1
DAC124_VREFIN: JP5.2, R84.2, U4.7 (VREFIN)
DAC_A: J6.2; also elsewhere on the board
DAC_A_JUMPERED: J6.1, U4.2 (VOUTA)
DAC_B: J7.2; also elsewhere on the board
DAC_B_JUMPERED: J7.1, U4.3 (VOUTB)
DAC_C: J10.2; also elsewhere on the board
DAC_C_JUMPERED: J10.1, U4.4 (VOUTC)
DAC_D: J11.2; also elsewhere on the board
DAC_D_JUMPERED: J11.1, U4.5 (VOUTD)
DAC_STM: J1.2; also elsewhere on the board
GND: C50.2, C52.2, C54.2, C55.2, C56.2, C58.2, C60.2, C62.2, C64.2, C66.2, C68.2, C70.2, C72.2, C74.2, C76.2, C78.2, C80.2, C81.2, C82.2, C84.2, C95.2, C122.2, C123.2, C124.2, C125.2, C126.2, C127.2, C128.2, C129.2, C130.2, C131.2, C132.2, C133.2, C134.2, C135.2, C136.2, JP5.1, R21.2, R109.2, TP44.TP, U4.6 (GND), U7.11 (GND), U8.11 (GND), U9.11 (GND), U10.11 (GND); also elsewhere on the board
NOT-USED-2: C136.1, R94.2, TP18.TP
NOT-USED-3: R21.1, R57.1, TP41.TP
PE11_DAC_SPI4_NSS: U4.9 (!SYNC!); also elsewhere on the board
PE12_DAC_SPI4_SCK: U4.10 (SCLK); also elsewhere on the board
PE14_DAC_SPI4_MOSI: U4.8 (DIN); also elsewhere on the board
STM_DAC: TP106.PAD, U7.12 (+V); also elsewhere on the board
STM_DAC-: C154.2, R109.1, R110.1, U7.13 (-V)
STM_DAC_OUT: C154.1, J1.1, R110.2, U7.14 (OUT)
V3.3A: C55.1, C56.1, C81.1, C82.1, U7.4 (VCC), U8.4 (VCC), U9.4 (VCC), U10.4 (VCC); also elsewhere on the board
V3.3DAC: C126.1, C127.1, R84.1, U4.1 (VA); also elsewhere on the board

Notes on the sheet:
OP-AMP buffer for STM DAC1
External DAC
Buffer for Internal DAC
External Voltage Reference Option
STM DAC output buffer can be scaled down and have single pole filter.
If ADC input is unused, pull input+ low with 1Meg resistor.
Snip Jumper and add resistor to add protection to DAC output if necessary.
Snip Jumper and add resistor to add protection to DAC output if necessary.

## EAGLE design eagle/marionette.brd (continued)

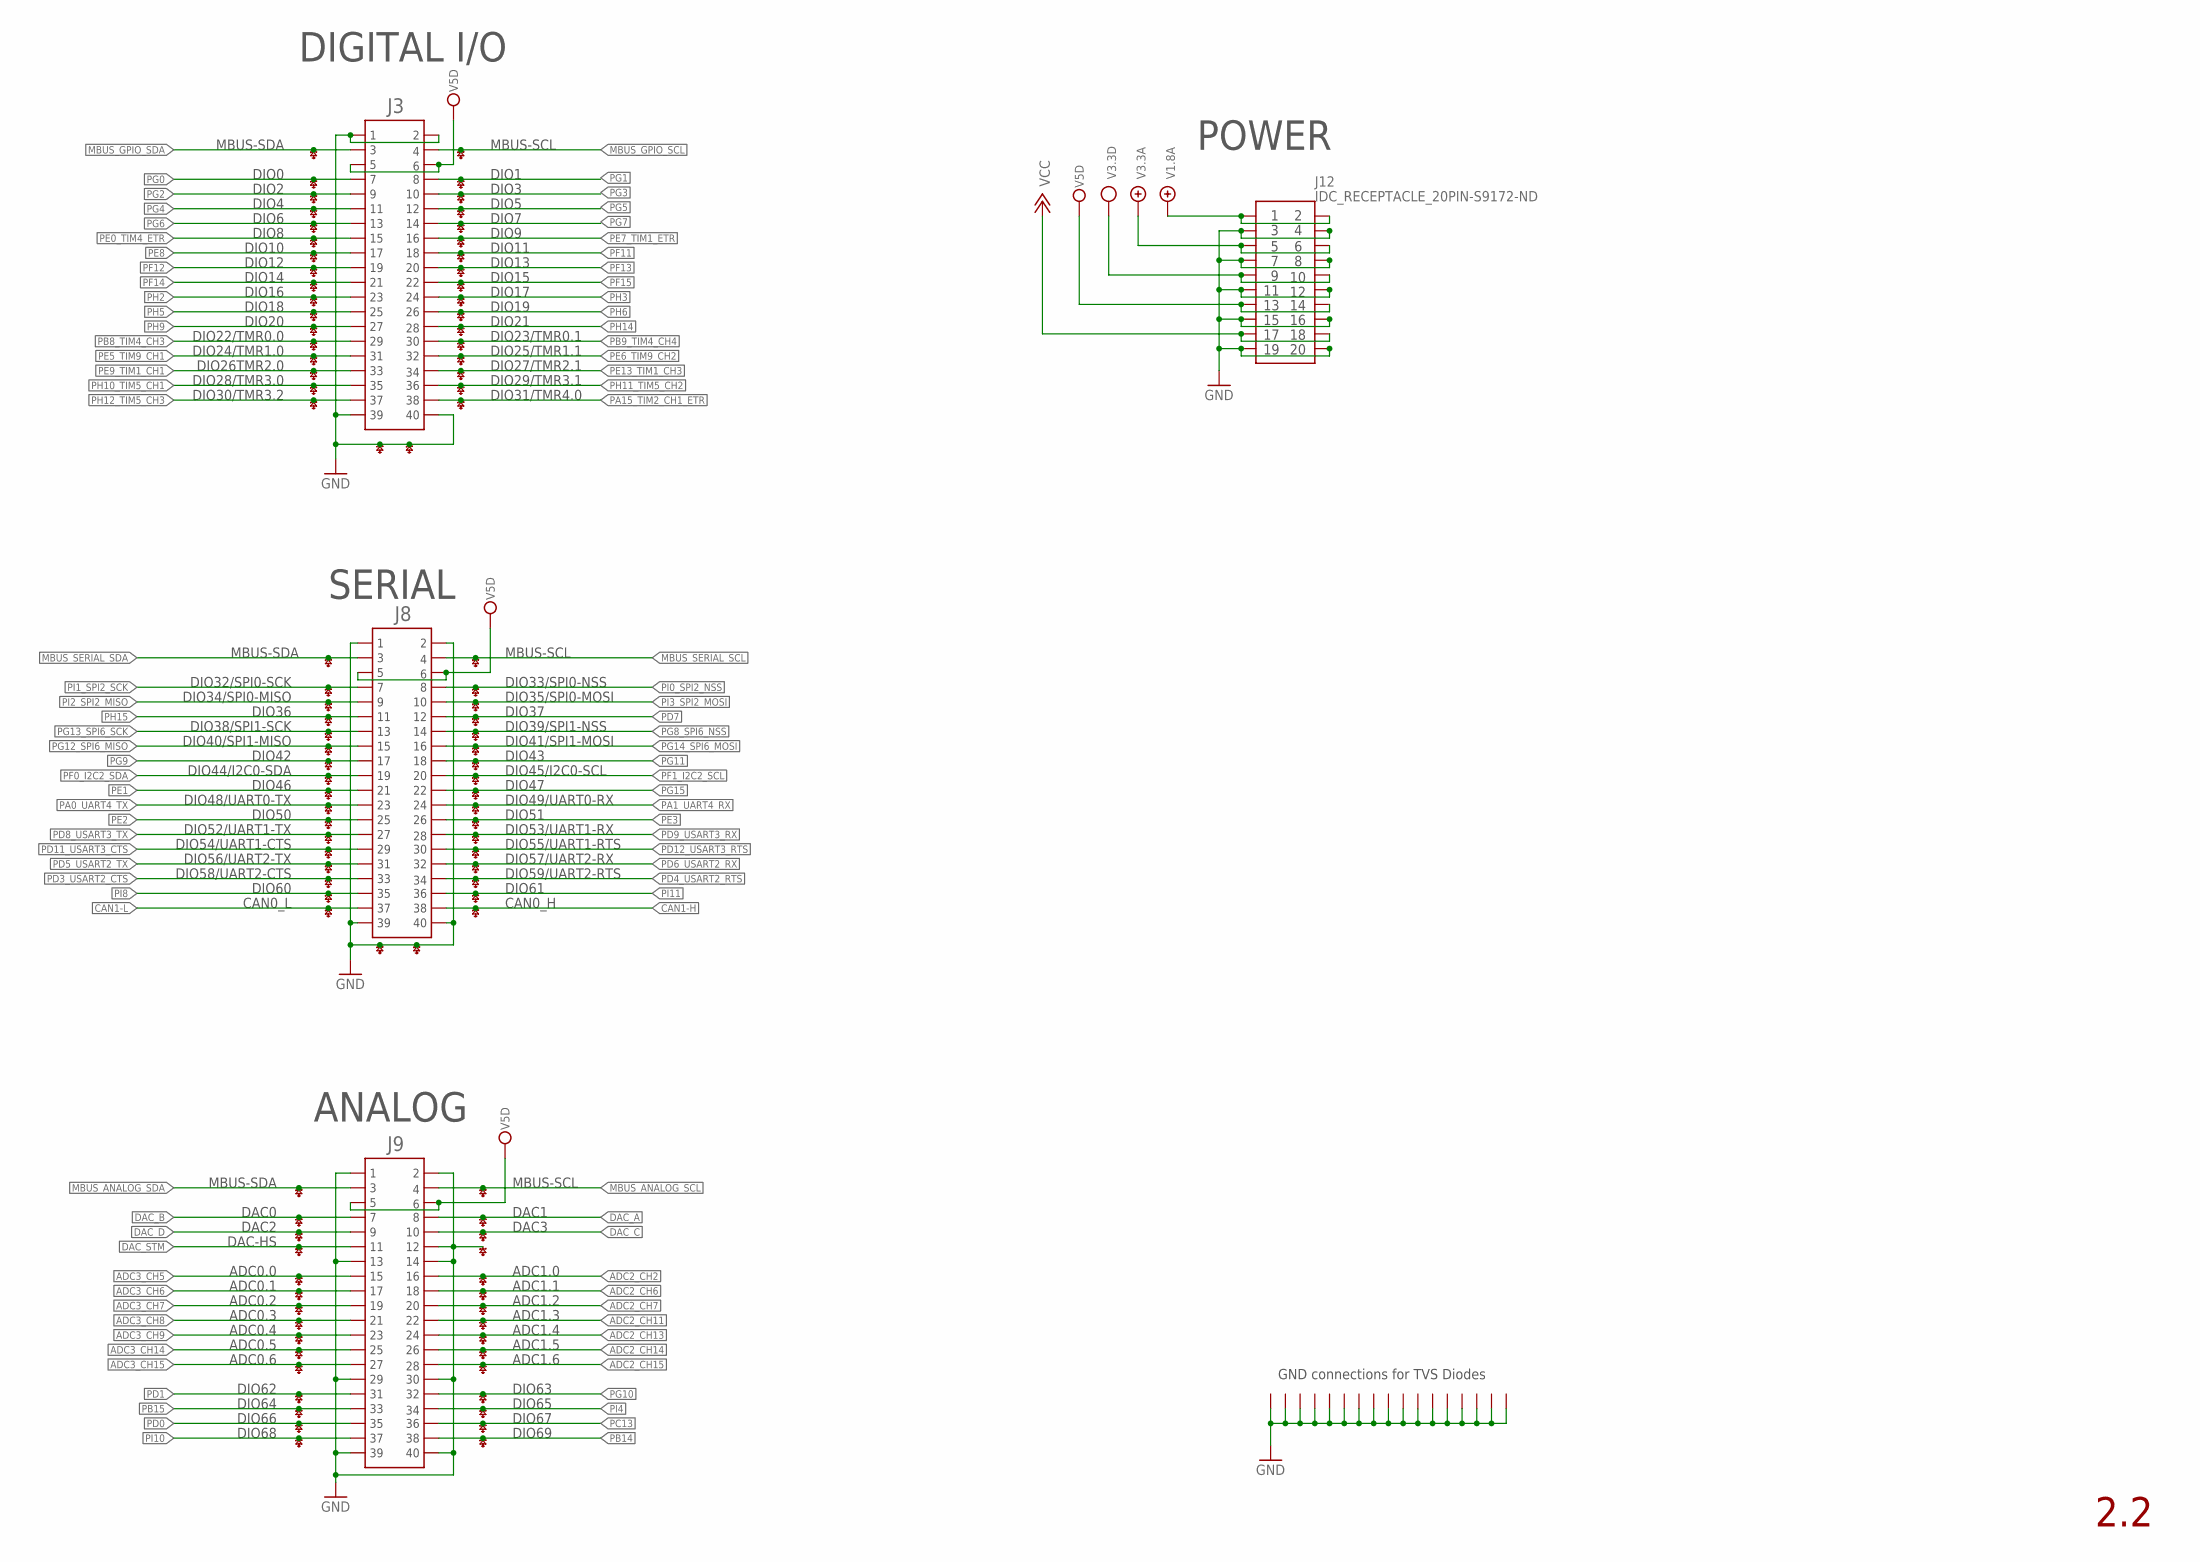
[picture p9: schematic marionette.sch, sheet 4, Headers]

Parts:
D1, D2, D4, D5, D6, D7, D8, D9, D10, D11, D12, D13, D14, D15, D16, D17, D18: ESD8006-ESD8006; UDFN-8-3.3X1.0_6MIL
J3, J8, J9: IDC_RECEPTACLE_2X20-S9175-ND; IDC_RECEPTACLES
J12: IDC_RECEPTACLE_20PIN-S9172-ND; IDC_RECEPTACLES_20PIN

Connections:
ADC2_CH2: D1.5 (CATHODE), J9.16; also elsewhere on the board
ADC2_CH6: D1.2 (CATHODE), J9.18; also elsewhere on the board
ADC2_CH7: D5.7 (CATHODE), J9.20; also elsewhere on the board
ADC2_CH11: D5.4 (CATHODE), J9.22; also elsewhere on the board
ADC2_CH13: D5.2 (CATHODE), J9.24; also elsewhere on the board
ADC2_CH14: D6.7 (CATHODE), J9.26; also elsewhere on the board
ADC2_CH15: D6.4 (CATHODE), J9.28; also elsewhere on the board
ADC3_CH5: D1.4 (CATHODE), J9.15; also elsewhere on the board
ADC3_CH6: D1.1 (CATHODE), J9.17; also elsewhere on the board
ADC3_CH7: D5.8 (CATHODE), J9.19; also elsewhere on the board
ADC3_CH8: D5.5 (CATHODE), J9.21; also elsewhere on the board
ADC3_CH9: D5.1 (CATHODE), J9.23; also elsewhere on the board
ADC3_CH14: D6.8 (CATHODE), J9.25; also elsewhere on the board
ADC3_CH15: D6.5 (CATHODE), J9.27; also elsewhere on the board
CAN1-H: D12.4 (CATHODE), J8.38; also elsewhere on the board
CAN1-L: D12.5 (CATHODE), J8.37; also elsewhere on the board
DAC_A: D2.5 (CATHODE), J9.8; also elsewhere on the board
DAC_B: D2.4 (CATHODE), J9.7; also elsewhere on the board
DAC_C: D2.2 (CATHODE), J9.10; also elsewhere on the board
DAC_D: D2.1 (CATHODE), J9.9; also elsewhere on the board
DAC_STM: D1.8 (CATHODE), J9.11; also elsewhere on the board
GND: D1.3 (PIN), D1.6 (PIN), D1.7 (CATHODE), D1.9 (PIN), D1.10 (PIN), D2.3 (PIN), D2.6 (PIN), D2.9 (PIN), D2.10 (PIN), D4.3 (PIN), D4.6 (PIN), D4.9 (PIN), D4.10 (PIN), D5.3 (PIN), D5.6 (PIN), D5.9 (PIN), D5.10 (PIN), D6.3 (PIN), D6.6 (PIN), D6.9 (PIN), D6.10 (PIN), D7.3 (PIN), D7.6 (PIN), D7.9 (PIN), D7.10 (PIN), D8.3 (PIN), D8.6 (PIN), D8.9 (PIN), D8.10 (PIN), D9.3 (PIN), D9.6 (PIN), D9.9 (PIN), D9.10 (PIN), D10.3 (PIN), D10.6 (PIN), D10.9 (PIN), D10.10 (PIN), D11.3 (PIN), D11.6 (PIN), D11.9 (PIN), D11.10 (PIN), D12.1 (CATHODE), D12.2 (CATHODE), D12.3 (PIN), D12.6 (PIN), D12.9 (PIN), D12.10 (PIN), D13.1 (CATHODE), D13.2 (CATHODE), D13.3 (PIN), D13.6 (PIN), D13.9 (PIN), D13.10 (PIN), D14.3 (PIN), D14.6 (PIN), D14.9 (PIN), D14.10 (PIN), D15.3 (PIN), D15.6 (PIN), D15.9 (PIN), D15.10 (PIN), D16.3 (PIN), D16.6 (PIN), D16.9 (PIN), D16.10 (PIN), D17.3 (PIN), D17.6 (PIN), D17.9 (PIN), D17.10 (PIN), D18.3 (PIN), D18.6 (PIN), D18.9 (PIN), D18.10 (PIN), J3.1, J3.2, J3.39, J3.40, J8.1, J8.2, J8.39, J8.40, J9.1, J9.2, J9.12, J9.13, J9.14, J9.29, J9.30, J9.39, J9.40, J12.3, J12.4, J12.7, J12.8, J12.11, J12.12, J12.15, J12.16, J12.19, J12.20; also elsewhere on the board
MBUS_ANALOG_SCL: D2.7 (CATHODE), J9.4; also elsewhere on the board
MBUS_ANALOG_SDA: D2.8 (CATHODE), J9.3; also elsewhere on the board
MBUS_GPIO_SCL: D18.8 (CATHODE), J3.4; also elsewhere on the board
MBUS_GPIO_SDA: D18.7 (CATHODE), J3.3; also elsewhere on the board
MBUS_SERIAL_SCL: D4.7 (CATHODE), J8.4; also elsewhere on the board
MBUS_SERIAL_SDA: D4.8 (CATHODE), J8.3; also elsewhere on the board
PA0_UART4_TX: D9.8 (CATHODE), J8.23; also elsewhere on the board
PA1_UART4_RX: D9.7 (CATHODE), J8.24; also elsewhere on the board
PA15_TIM2_CH1_ETR: D13.4 (CATHODE), J3.38; also elsewhere on the board
PB8_TIM4_CH3: D14.8 (CATHODE), J3.29; also elsewhere on the board
PB9_TIM4_CH4: D14.7 (CATHODE), J3.30; also elsewhere on the board
PB14: D7.2 (CATHODE), J9.38; also elsewhere on the board
PB15: D7.8 (CATHODE), J9.33; also elsewhere on the board
PC13: D7.4 (CATHODE), J9.36; also elsewhere on the board
PD0: D7.5 (CATHODE), J9.35; also elsewhere on the board
PD1: D6.1 (CATHODE), J9.31; also elsewhere on the board
PD3_USART2_CTS: D11.1 (CATHODE), J8.33; also elsewhere on the board
PD4_USART2_RTS: D11.2 (CATHODE), J8.34; also elsewhere on the board
PD5_USART2_TX: D11.5 (CATHODE), J8.31; also elsewhere on the board
PD6_USART2_RX: D11.4 (CATHODE), J8.32; also elsewhere on the board
PD7: D8.7 (CATHODE), J8.12; also elsewhere on the board
PD8_USART3_TX: D9.1 (CATHODE), J8.27; also elsewhere on the board
PD9_USART3_RX: D9.2 (CATHODE), J8.28; also elsewhere on the board
PD11_USART3_CTS: D11.8 (CATHODE), J8.29; also elsewhere on the board
PD12_USART3_RTS: D11.7 (CATHODE), J8.30; also elsewhere on the board
PE0_TIM4_ETR: D17.1 (CATHODE), J3.15; also elsewhere on the board
PE1: D10.1 (CATHODE), J8.21; also elsewhere on the board
PE2: D9.5 (CATHODE), J8.25; also elsewhere on the board
PE3: D9.4 (CATHODE), J8.26; also elsewhere on the board
PE5_TIM9_CH1: D14.5 (CATHODE), J3.31; also elsewhere on the board
PE6_TIM9_CH2: D14.4 (CATHODE), J3.32; also elsewhere on the board
PE7_TIM1_ETR: D17.2 (CATHODE), J3.16; also elsewhere on the board
PE8: D16.8 (CATHODE), J3.17; also elsewhere on the board
PE9_TIM1_CH1: D14.1 (CATHODE), J3.33; also elsewhere on the board
PE13_TIM1_CH3: D14.2 (CATHODE), J3.34; also elsewhere on the board
PF0_I2C2_SDA: D10.5 (CATHODE), J8.19; also elsewhere on the board
PF1_I2C2_SCL: D10.4 (CATHODE), J8.20; also elsewhere on the board
PF11: D16.7 (CATHODE), J3.18; also elsewhere on the board
PF12: D16.5 (CATHODE), J3.19; also elsewhere on the board
PF13: D16.4 (CATHODE), J3.20; also elsewhere on the board
PF14: D16.1 (CATHODE), J3.21; also elsewhere on the board
PF15: D16.2 (CATHODE), J3.22; also elsewhere on the board
PG0: D18.5 (CATHODE), J3.7; also elsewhere on the board
PG1: D18.4 (CATHODE), J3.8; also elsewhere on the board
PG2: D18.2 (CATHODE), J3.9; also elsewhere on the board
PG3: D18.1 (CATHODE), J3.10; also elsewhere on the board
PG4: D17.8 (CATHODE), J3.11; also elsewhere on the board
PG5: D17.7 (CATHODE), J3.12; also elsewhere on the board
PG6: D17.5 (CATHODE), J3.13; also elsewhere on the board
PG7: D17.4 (CATHODE), J3.14; also elsewhere on the board
PG8_SPI6_NSS: D8.4 (CATHODE), J8.14; also elsewhere on the board
PG9: D10.8 (CATHODE), J8.17; also elsewhere on the board
PG10: D6.2 (CATHODE), J9.32; also elsewhere on the board
PG11: D10.7 (CATHODE), J8.18; also elsewhere on the board
PG12_SPI6_MISO: D8.1 (CATHODE), J8.15; also elsewhere on the board
PG13_SPI6_SCK: D8.5 (CATHODE), J8.13; also elsewhere on the board
PG14_SPI6_MOSI: D8.2 (CATHODE), J8.16; also elsewhere on the board
PG15: D10.2 (CATHODE), J8.22; also elsewhere on the board
PH2: D15.8 (CATHODE), J3.23; also elsewhere on the board
PH3: D15.7 (CATHODE), J3.24; also elsewhere on the board
PH5: D15.5 (CATHODE), J3.25; also elsewhere on the board
PH6: D15.4 (CATHODE), J3.26; also elsewhere on the board
PH9: D15.1 (CATHODE), J3.27; also elsewhere on the board
PH10_TIM5_CH1: D13.8 (CATHODE), J3.35; also elsewhere on the board
PH11_TIM5_CH2: D13.7 (CATHODE), J3.36; also elsewhere on the board
PH12_TIM5_CH3: D13.5 (CATHODE), J3.37; also elsewhere on the board
PH14: D15.2 (CATHODE), J3.28; also elsewhere on the board
PH15: D8.8 (CATHODE), J8.11; also elsewhere on the board
PI0_SPI2_NSS: D4.5 (CATHODE), J8.8; also elsewhere on the board
PI1_SPI2_SCK: D4.4 (CATHODE), J8.7; also elsewhere on the board
PI2_SPI2_MISO: D4.1 (CATHODE), J8.9; also elsewhere on the board
PI3_SPI2_MOSI: D4.2 (CATHODE), J8.10; also elsewhere on the board
PI4: D7.7 (CATHODE), J9.34; also elsewhere on the board
PI8: D12.8 (CATHODE), J8.35; also elsewhere on the board
PI10: D7.1 (CATHODE), J9.37; also elsewhere on the board
PI11: D12.7 (CATHODE), J8.36; also elsewhere on the board
V1.8A: J12.1, J12.2; also elsewhere on the board
V3.3A: J12.5, J12.6; also elsewhere on the board
V3.3D: J12.9, J12.10; also elsewhere on the board
V5D: J3.5, J3.6, J8.5, J8.6, J9.5, J9.6, J12.13, J12.14; also elsewhere on the board
VCC: J12.17, J12.18; also elsewhere on the board

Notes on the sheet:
POWER
GND connections for TVS Diodes
DIO22/TMR0.0
DIO23/TMR0.1
DIO24/TMR1.0
DIO25/TMR1.1
DIO26TMR2.0
DIO27/TMR2.1
DIO28/TMR3.0
DIO29/TMR3.1
DIO30/TMR3.2
DIO31/TMR4.0
DAC0
DAC1
DAC2
DAC3
DAC-HS
ADC1.0
ADC1.1
ADC1.2
ADC1.3
ADC1.4
ADC1.5
ADC0.0
ADC0.1
ADC0.2
ADC0.3
ADC0.4
ADC0.5
DIO32/SPI0-SCK
DIO34/SPI0-MISO
DIO35/SPI0-MOSI
DIO33/SPI0-NSS
DIO38/SPI1-SCK
DIO40/SPI1-MISO
DIO41/SPI1-MOSI
DIO39/SPI1-NSS
DIO44/I2C0-SDA
DIO45/I2C0-SCL
CAN0_L

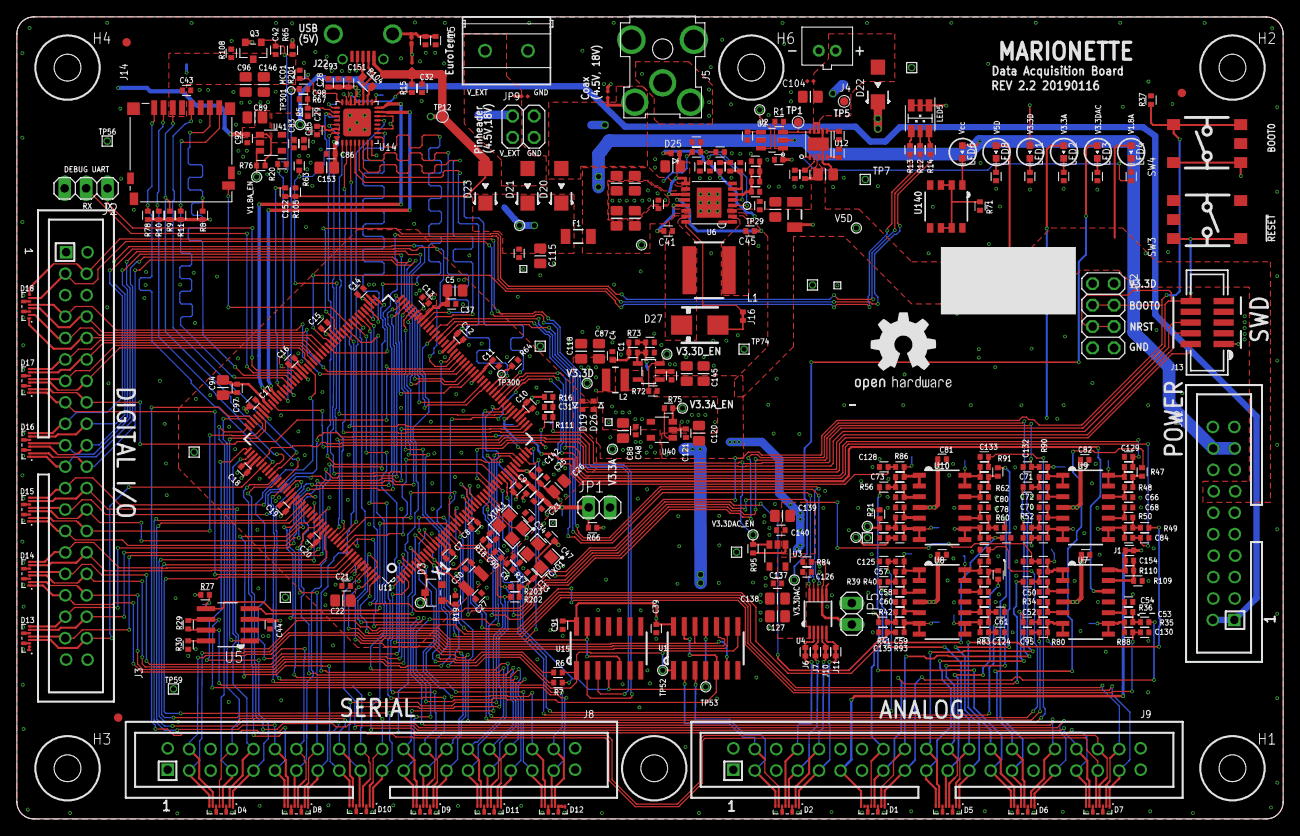
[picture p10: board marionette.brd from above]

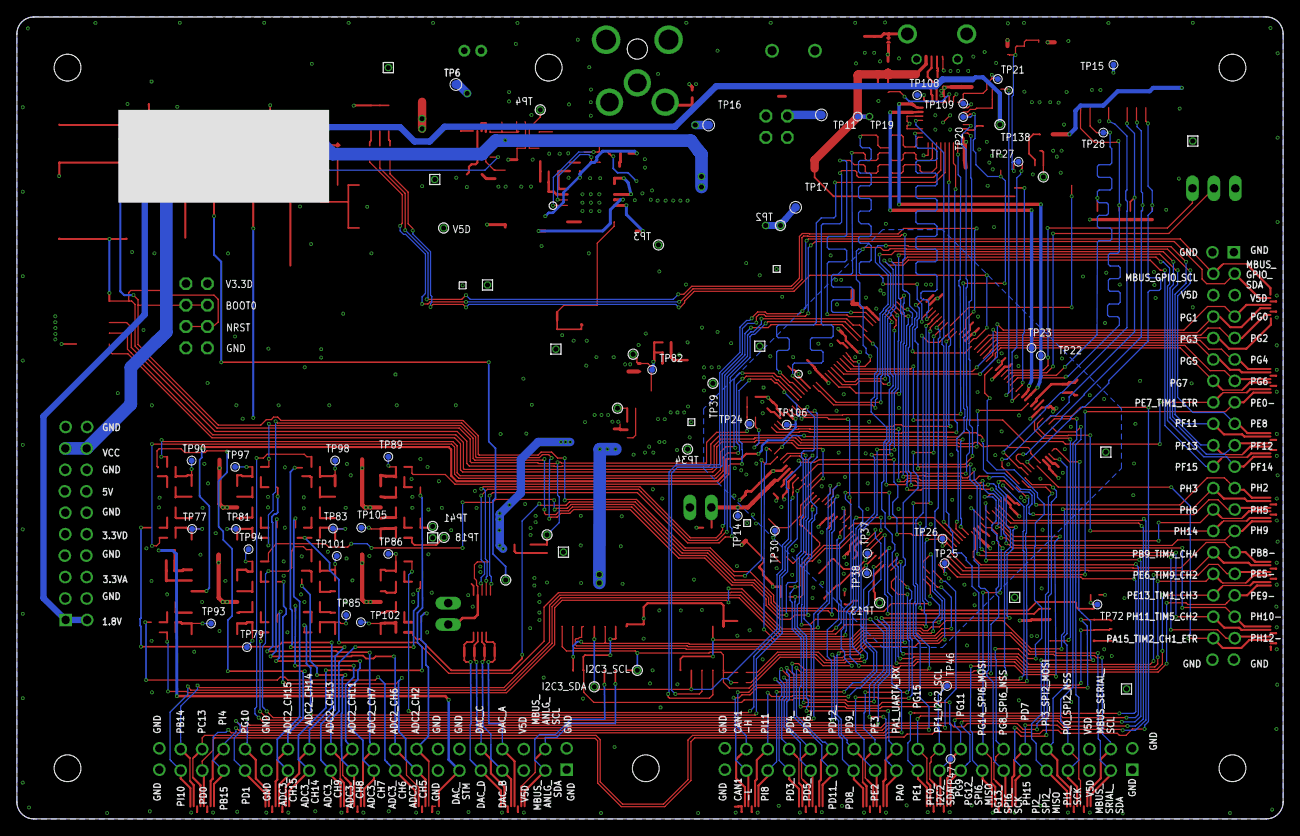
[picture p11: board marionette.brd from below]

Board: 4 copper layers, 150.0 x 95.0 mm, 437 parts (50 on the bottom side), 289 nets.

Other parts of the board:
U$1: OSHW1

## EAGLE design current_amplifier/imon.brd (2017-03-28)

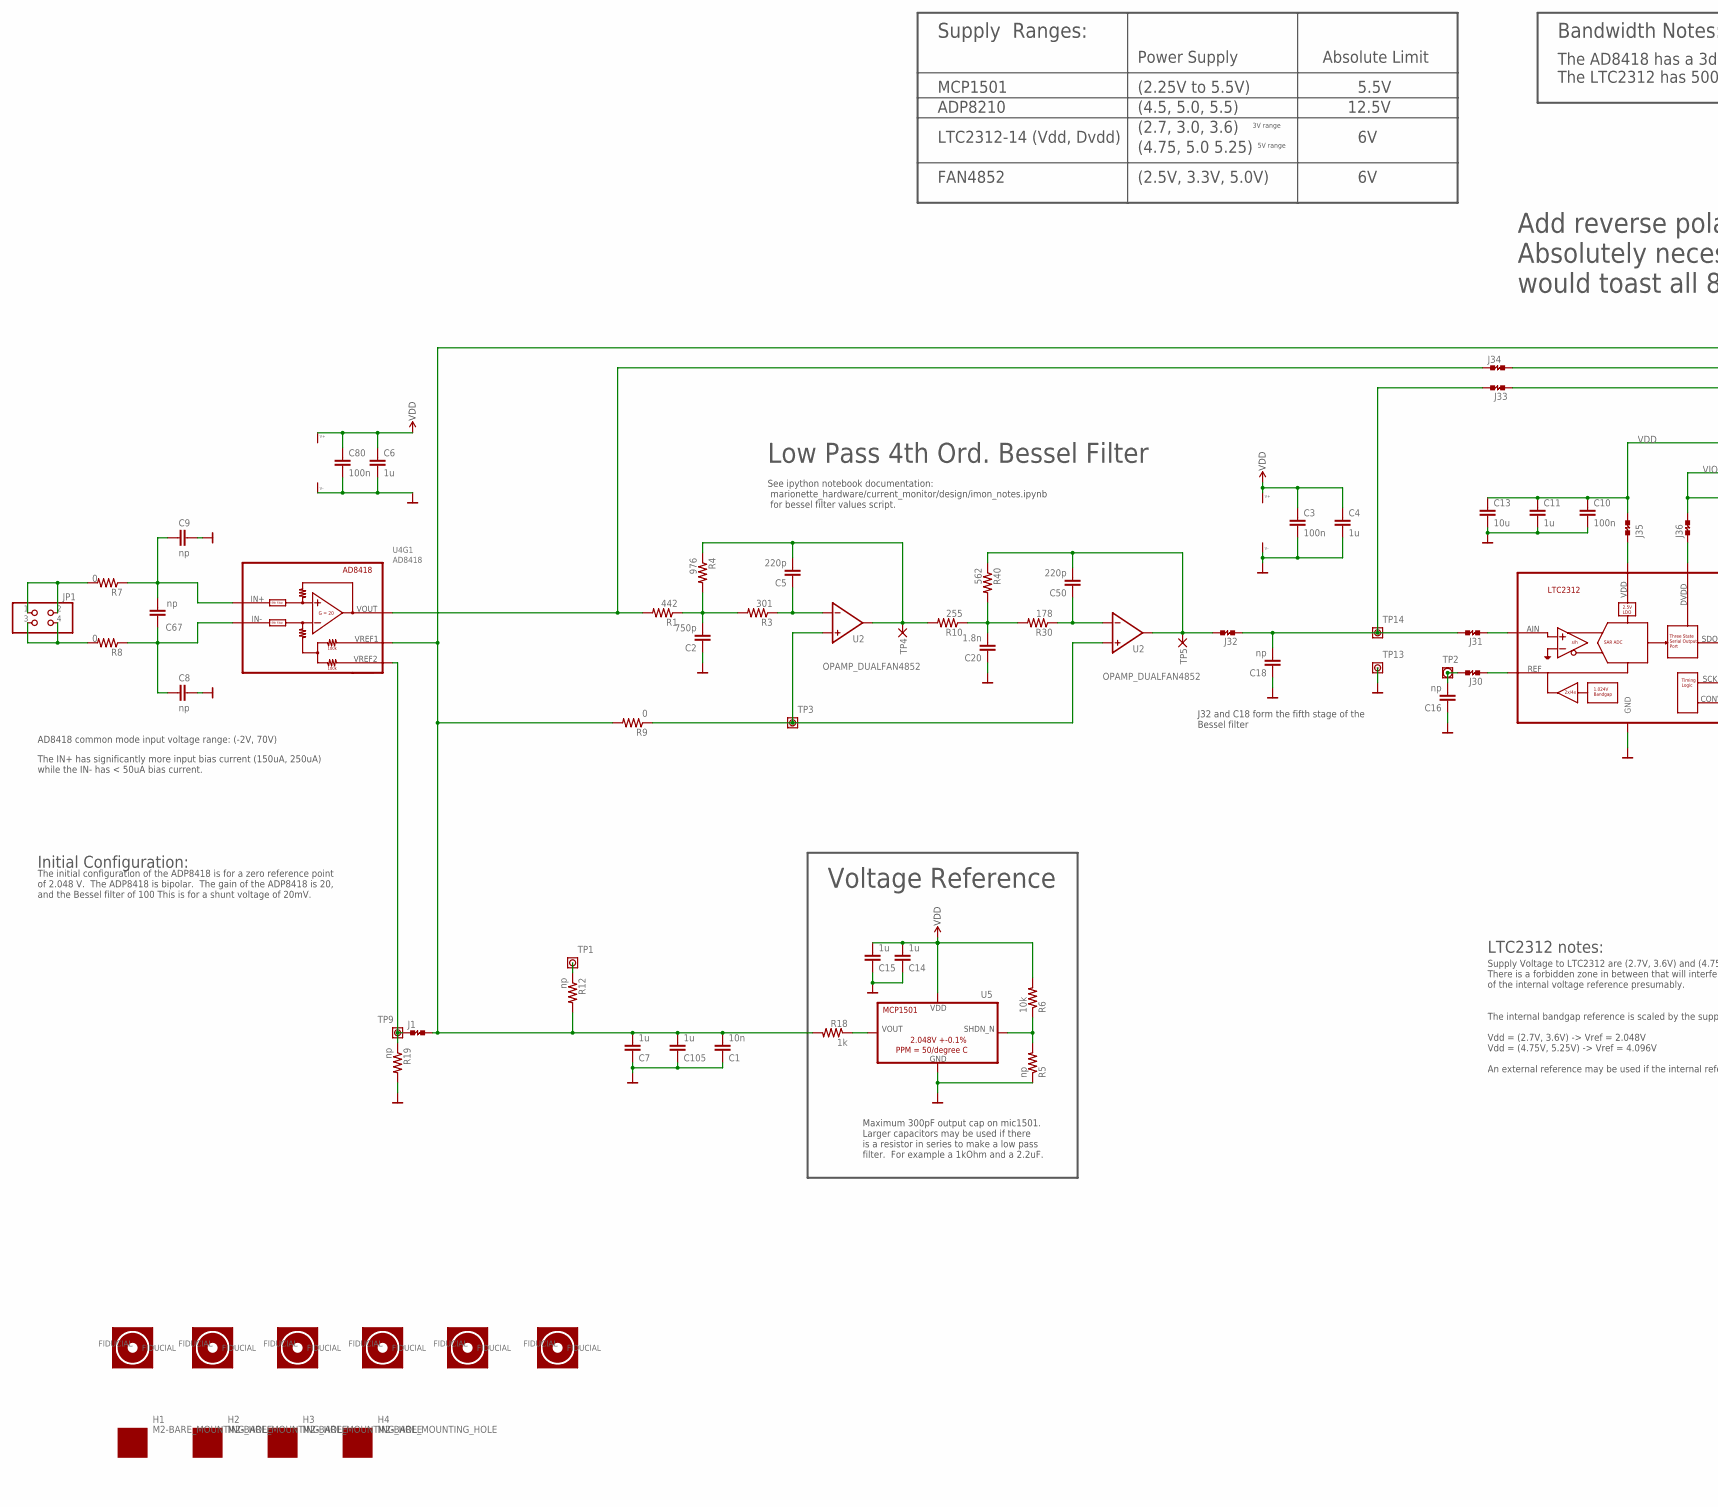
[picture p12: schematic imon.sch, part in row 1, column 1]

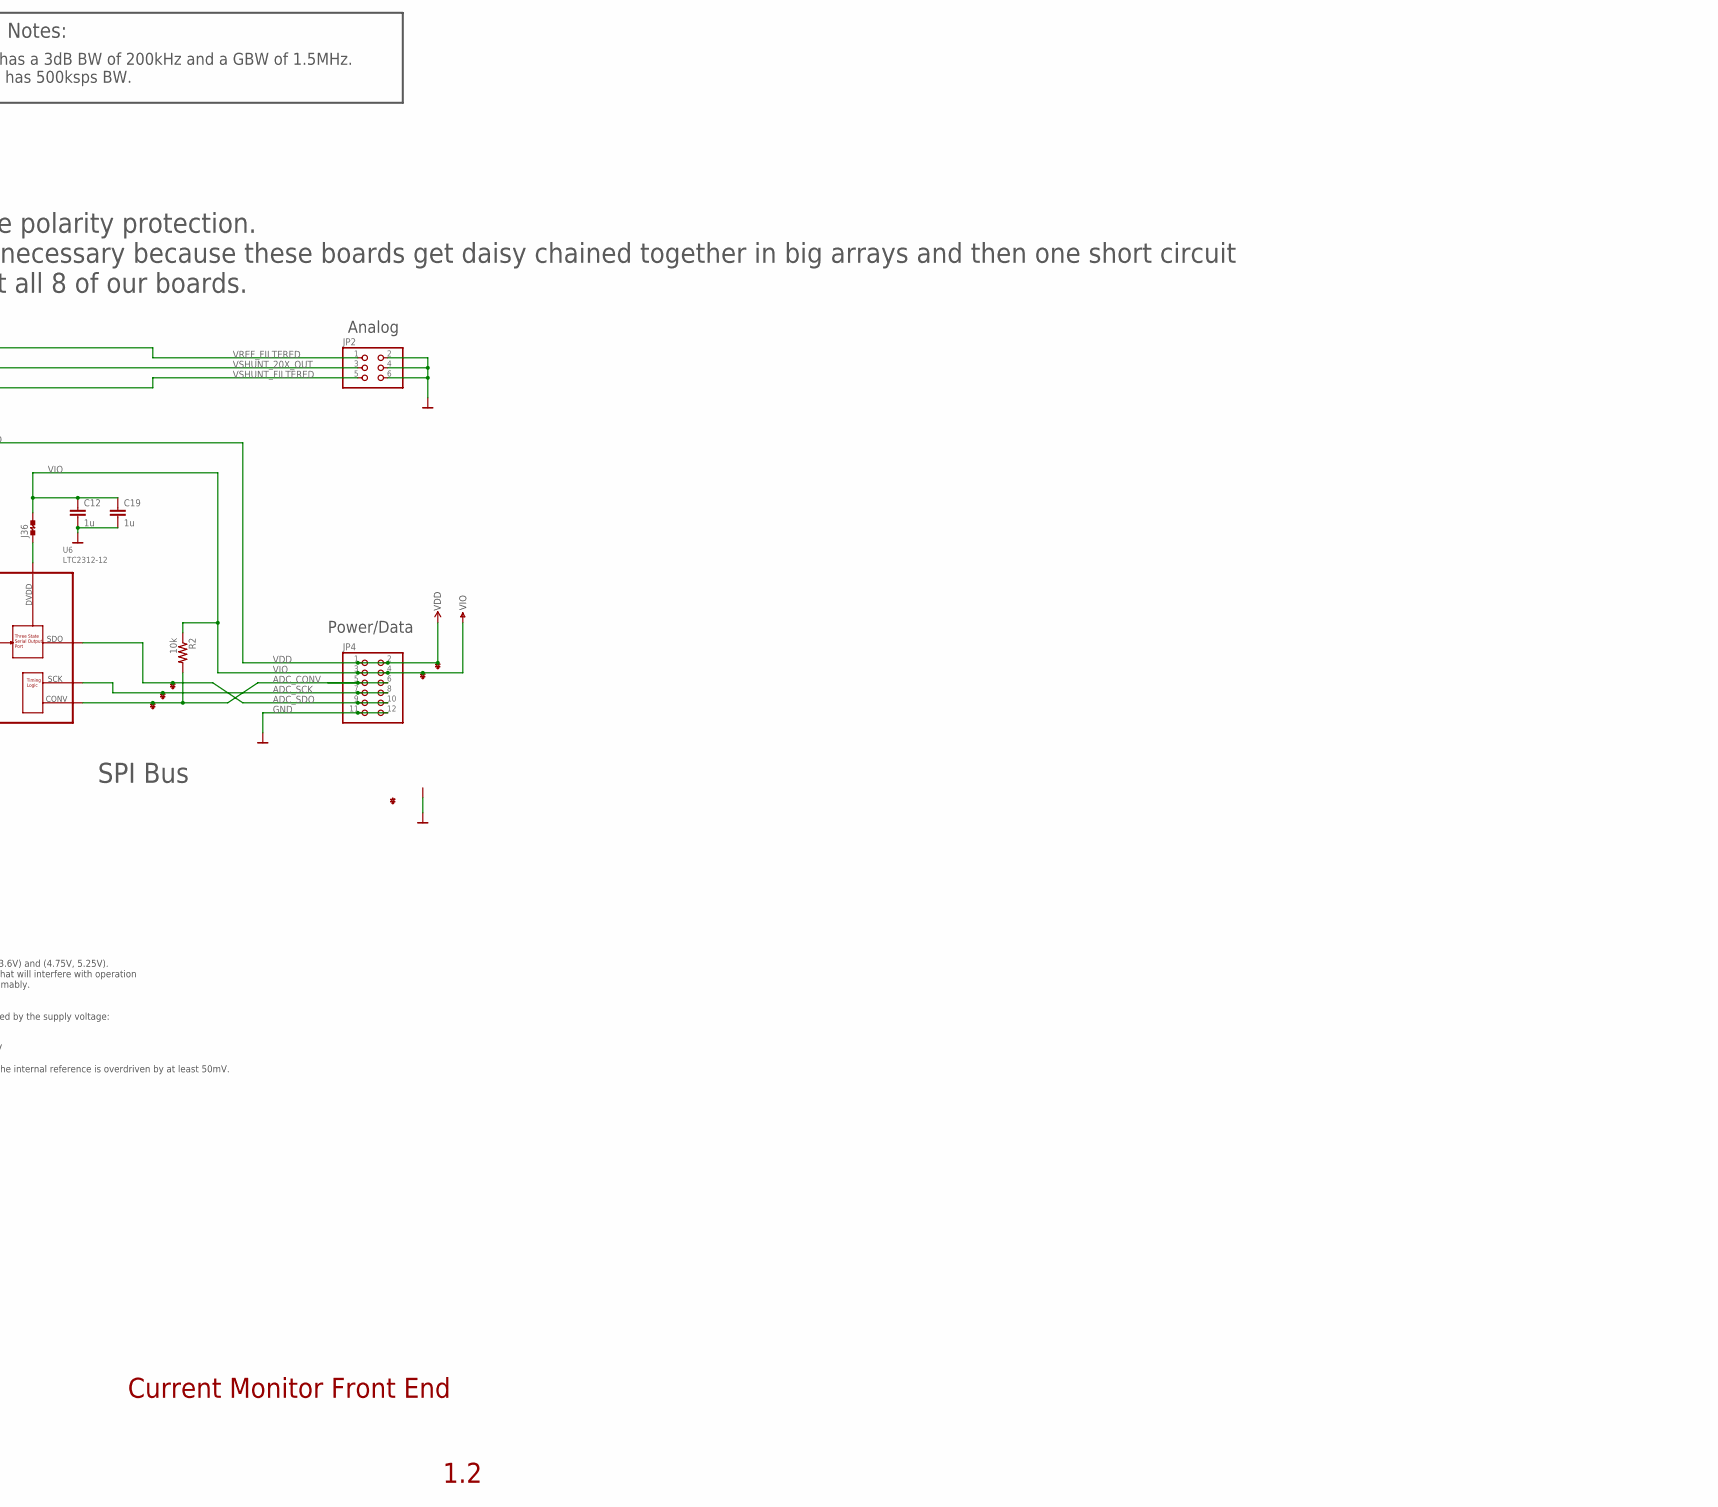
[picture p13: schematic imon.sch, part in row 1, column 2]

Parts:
C1: 10n; .0402-B
C2: 750p; .0402-B
C3, C10, C80: 100n; .0402-B
C4, C6, C7, C11, C12, C14, C15, C19, C105: 1u; .0402-B
C5, C50: 220p; .0402-B
C8, C9: np; .0805-A-NOSILK
C13: 10u; .0805-B
C16, C18: np; .0402-B
C20: 1.8n; .0402-B
C67: np; 1206-0402
D1: ESD8006-ESD8006; UDFN-8-3.3X1.0_6MIL
FIDUCIAL1, FIDUCIAL2, FIDUCIAL3, FIDUCIAL4, FIDUCIAL5, FIDUCIAL6: FIDUCIAL-1.0X2.5
H1, H2, H3, H4: M2-BARE_MOUNTING_HOLE
J1, J30, J31, J32, J33, J34: JUMPER-SHORTED-CUTTABLE-E0402-0.3MM
J35, J36: JUMPER-SHORTED-CUTTABLE-E0603-0.8MM
JP1: PINHD-2X2; 2X02
JP2: PINHD-2X3; 2X03
JP4: PINHD-2X6/90; 2X06/90
R1: 442; .0402-B
R2, R6: 10k; .0402-B
R3: 301; .0402-B
R4: 976; .0402-B
R5, R12, R19: np; .0402-B
R7, R8: 0; 1206-0402
R9: 0; .0402-B
R10: 255; .0402-B
R18: 1k; .0402-B
R30: 178; .0402-B
R40: 562; .0402-B
TP1, TP9, TP14: PAD+VIA_0.25MM
TP2: PAD+VIA_0.6MM
TP3: PAD+VIA_0.3302MM
TP4, TP5: PAD+X-1.0-NO_CREAM+SILK; PAD-ROUND-1.0-NOCREAM+SILK
TP13: PAD+VIA_GND_0.25MM; PAD+GND_VIA_0.25MM
U2: OPAMP_DUALFAN4852; MSOP-8
U4: AD8418; SOIC-8_BETTER_TOE
U5: MCP1501"; SOT23-6
U6: LTC2312-12; TSOT23-8

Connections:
AD8418_REF2: J1.1, R19.1, TP9.TP, U4.3 (VREF2)
ADC_AIN: J31.1, U6.4 (AIN)
ADC_CONV: D1.4 (CATHODE), JP4.5, JP4.6, R2.2, U6.8 (CONV)
ADC_SCK: D1.2 (CATHODE), JP4.7, JP4.8, U6.7 (SCK)
ADC_SDO: D1.1 (CATHODE), JP4.9, JP4.10, U6.6 (SDO)
ADC_VREF: C16.2, J30.2, TP2.TP
ADC_VREF_CUTTABLE: J30.1, U6.2 (REF)
FILTER1-: C5.1, R3.1, U2.2 (-IN)
FILTER2-: C50.1, R30.1, U2.6 (-IN)
FILTER_1_OUT: C5.2, R4.1, R10.2, TP4.PAD, U2.1 (OUT)
FILTER_1_V1: C2.2, R1.1, R3.2, R4.2
FILTER_2_OUT: C50.2, J32.2, R40.1, TP5.PAD, U2.7 (OUT)
FILTER_2_V1: C20.2, R10.1, R30.2, R40.2
GND: C1.1, C2.1, C3.2, C4.2, C6.2, C7.1, C8.1, C9.1, C10.2, C11.2, C12.2, C13.2, C14.1, C15.1, C16.1, C18.1, C19.2, C20.1, C80.2, C105.1, D1.3 (PIN), D1.6 (PIN), D1.9 (PIN), D1.10 (PIN), JP2.2, JP2.4, JP2.6, JP4.11, JP4.12, R5.1, R19.2, TP13.TP, U2.4 (V-), U4.2 (V-), U5.2 (GND), U5.3 (GND), U5.5 (GND), U6.3 (GND)
MCP1501_SHDN_N: R5.2, R6.1, U5.4 (SHDN_N)
OPAMP_IN+: R9.1, TP3.TP, U2.3 (+IN), U2.5 (+IN)
V3.3D_CUTTABLE: J36.1, U6.5 (DVDD)
V5D_CUTTABLE: J35.1, U6.1 (VDD)
VDD: C3.1, C4.1, C6.1, C10.1, C11.1, C13.1, C14.2, C15.2, C80.1, D1.8 (CATHODE), J35.2, JP4.1, JP4.2, R6.2, U2.8 (V+), U4.6 (V+), U5.6 (VDD)
VIO: C12.1, C19.1, D1.7 (CATHODE), J36.2, JP4.3, JP4.4, R2.1
VREF_FILTERED: C1.2, C7.2, C105.2, J1.2, JP2.1, R9.2, R12.2, R18.2, U4.7 (VREF1)
VREF_OPTIONAL: R12.1, TP1.TP
VREF_OUT: R18.1, U5.1 (VOUT)
VSHUNT_20X: J34.1, R1.2, U4.5 (VOUT)
VSHUNT_20X_OUT: J34.2, JP2.3
VSHUNT_FILTERED: J33.1, JP2.5
VSHUNT_FILTERED_ADC: C18.2, J31.2, J32.1, J33.2, TP14.TP
VSHUNT_FILTERED_M: C8.2, C67.1, R8.1, U4.1 (IN-)
VSHUNT_FILTERED_P: C9.2, C67.2, R7.1, U4.8 (IN+)
VSHUNT_M: JP1.3, JP1.4, R8.2
VSHUNT_P: JP1.1, JP1.2, R7.2

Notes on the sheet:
Supply Ranges:
ADP8210
Power Supply
Absolute Limit
MCP1501
LTC2312-14 (Vdd, Dvdd)
(2.25V to 5.5V)
5.5V
12.5V
(4.5, 5.0, 5.5)
(2.7, 3.0, 3.6)
(4.75, 5.0 5.25)
3V range
5V range
SPI Bus
Low Pass 4th Ord. Bessel Filter
Maximum 300pF output cap on mic1501. Larger capacitors may be used if there is a resistor in series to make a low pass filter. For example a 1kOhm and a 2.2uF.
Current Monitor Front End
LTC2312 notes:
Supply Voltage to LTC2312 are (2.7V, 3.6V) and (4.75V, 5.25V). There is a forbidden zone in between that will interfere with operation of the internal voltage reference presumably.
The internal bandgap reference is scaled by the supply voltage: Vdd = (2.7V, 3.6V) -> Vref = 2.048V Vdd = (4.75V, 5.25V) -> Vref = 4.096V An external reference may be used if the internal reference is overdriven by at least 50mV.
See ipython notebook documentation: marionette_hardware/current_monitor/design/imon_notes.ipynb for bessel filter values script.
Initial Configuration:
The initial configuration of the ADP8418 is for a zero reference point of 2.048 V. The ADP8418 is bipolar. The gain of the ADP8418 is 20, and the Bessel filter of 100 This is for a shunt voltage of 20mV.
FAN4852
(2.5V, 3.3V, 5.0V)
J32 and C18 form the fifth stage of the Bessel filter
Power/Data
Analog
Bandwidth Notes:
The AD8418 has a 3dB BW of 200kHz and a GBW of 1.5MHz. The LTC2312 has 500ksps BW.
Voltage Reference
AD8418 common mode input voltage range: (-2V, 70V)
The IN+ has significantly more input bias current (150uA, 250uA) while the IN- has < 50uA bias current.
Add reverse polarity protection. Absolutely necessary because these boards get daisy chained together in big arrays and then one short circuit would toast all 8 of our boards.

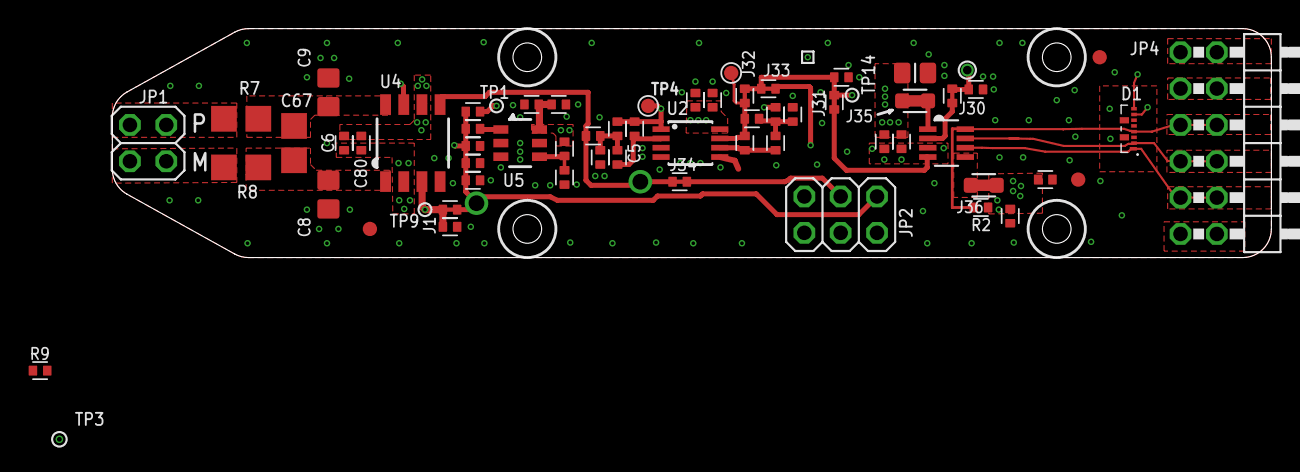
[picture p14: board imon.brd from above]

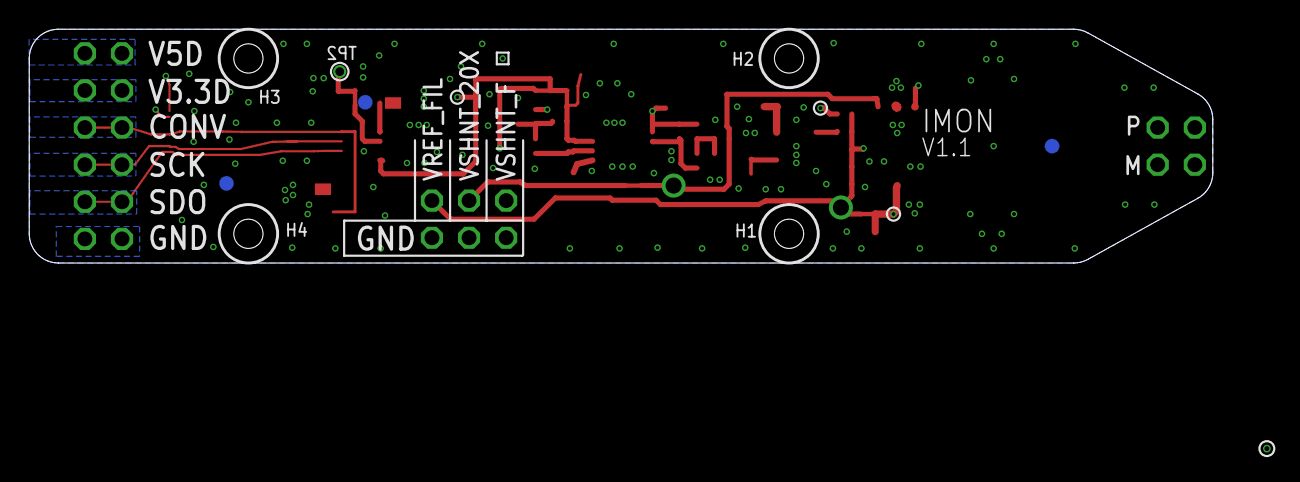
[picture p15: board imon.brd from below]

Board: 4 copper layers, 81.0 x 16.0 mm, 72 parts (3 on the bottom side), 31 nets.

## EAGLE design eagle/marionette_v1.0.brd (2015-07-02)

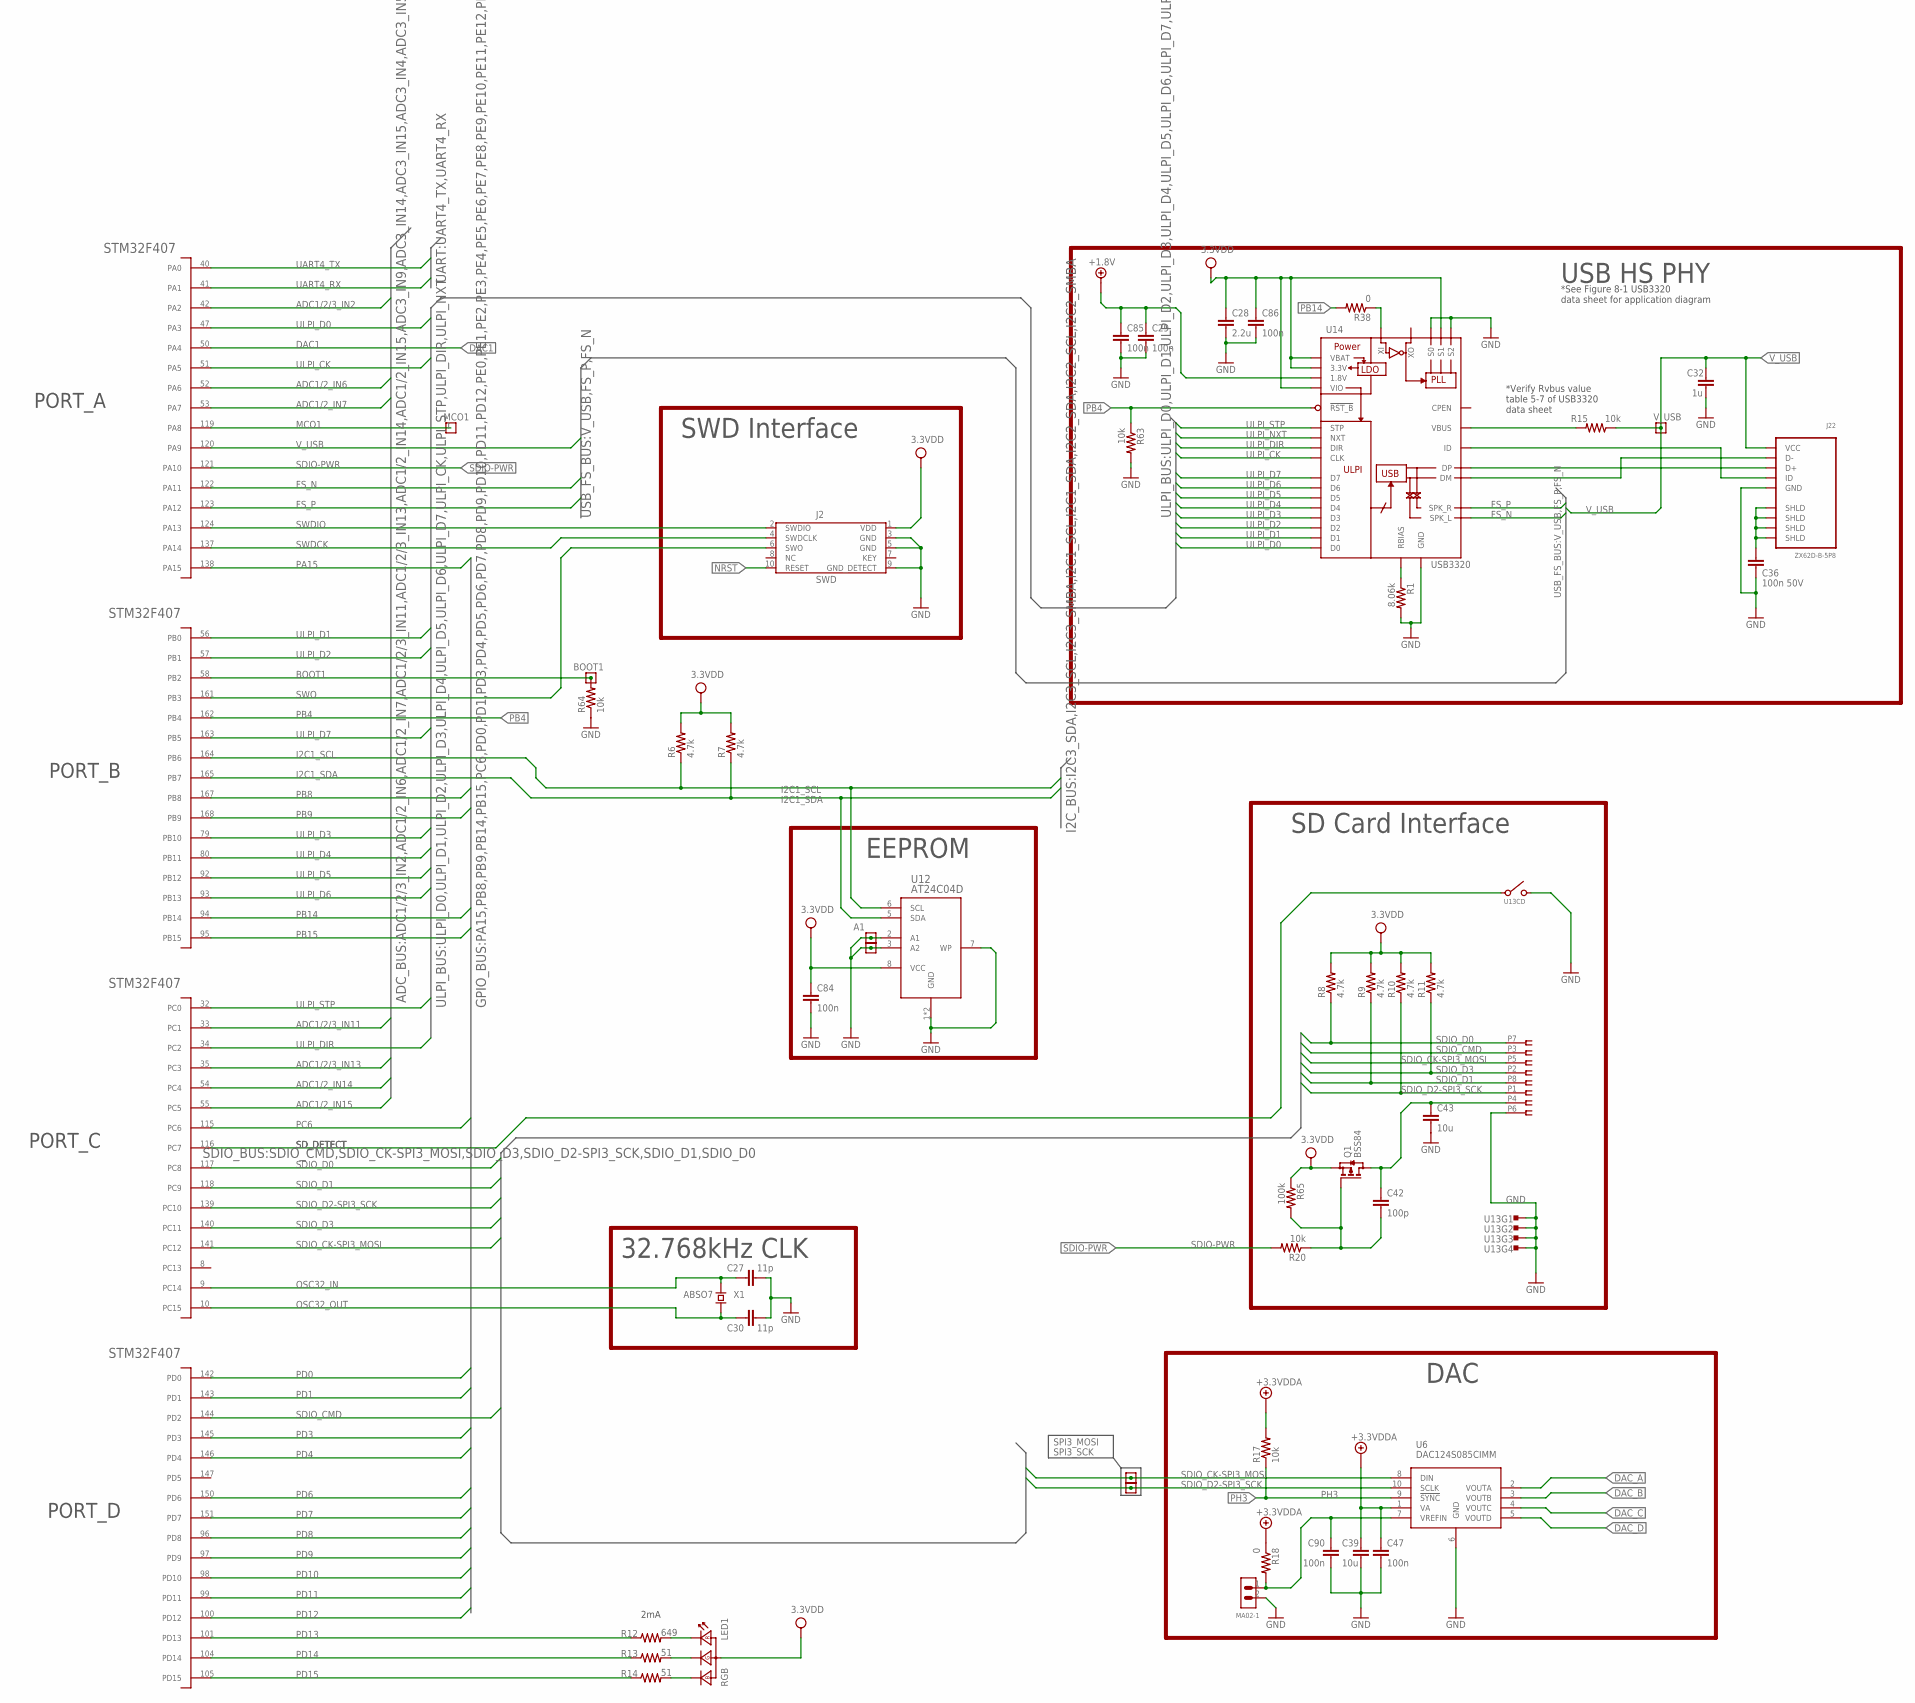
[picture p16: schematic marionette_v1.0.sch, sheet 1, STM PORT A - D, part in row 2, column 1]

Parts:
A1, A2: TEST-POINT10MIL-TEST-POINT; 10MIL-TEST-POINT
BOOT1: TEST-POINT10MIL-TEST-POINT; 10MIL-TEST-POINT
C27, C30: 11p; .0603-C
C28: 2.2u; .0603-C
C29, C47, C84, C85, C86, C90: 100n; .0603-C
C32: 1u; .0603-C
C36: 100n 50V; .0603-C
C39, C43: 10u; .0805-C-NOSILK
C42: 100p; .0603-C
J2: SWD; 2X10_BOXHEADER
J7: MA02-1
J22: ZX62D-B-5P8
LED1: RGB; KINGBRITE_RGBLED_1.6X1.26
MCO1: TEST-POINT10MIL-TEST-POINT; 10MIL-TEST-POINT
Q1: BSS84; SOT23
R1: 8.06k; .0603-C
R6, R7, R8, R9, R10, R11: 4.7k; .0603-C
R12: 649; .0603-C
R13, R14: 51; .0603-C
R15, R17, R20, R63, R64: 10k; .0603-C
R18, R38: 0; .0603-C
R65: 100k; .0603-C
SPI3_MOSI, SPI3_SCK: TEST-POINT10MIL-TEST-POINT; 10MIL-TEST-POINT
U1: STM32F407; LQFP176
U6: DAC124S085CIMM; 10-TFSOP
U12: AT24C04D; SO08
U13: CON_HIROSE_DM3D(MICROSD); HIROSE_DM3D(MICRO-SD)
U14: USB3320; QFN32-5X5
V_USB: TEST-POINT10MIL-TEST-POINT; 10MIL-TEST-POINT
X1: ABSO7; 2-SMD_ABM7

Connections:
3.3VDD: C28.1, C84.1, C86.1, J2.1 (VDD), LED1.2 (COMMON_ANODE), Q1.2 (S), R6.2, R7.2, R8.2, R9.2, R10.2, R11.2, R65.1, U12.8 (VCC), U14.11 (S1), U14.20 (3.3V), U14.21 (VBAT), U14.32 (VIO); also elsewhere on the board
+1.8V: C29.1, C85.1, U14.28 (1.8V), U14.30 (1.8V); also elsewhere on the board
+3.3VDDA: C39.1, C47.1, R17.2, R18.1, U6.1 (VA); also elsewhere on the board
ADC1/2/3_IN2: U1.42 (PA2); also elsewhere on the board
ADC1/2/3_IN11: U1.33 (PC1); also elsewhere on the board
ADC1/2/3_IN13: U1.35 (PC3); also elsewhere on the board
ADC1/2_IN6: U1.52 (PA6); also elsewhere on the board
ADC1/2_IN7: U1.53 (PA7); also elsewhere on the board
ADC1/2_IN14: U1.54 (PC4); also elsewhere on the board
ADC1/2_IN15: U1.55 (PC5); also elsewhere on the board
BOOT1: BOOT1.P$1, R64.2, U1.58 (PB2)
DAC1: U1.50 (PA4); also elsewhere on the board
DAC_A: U6.2 (VOUTA); also elsewhere on the board
DAC_B: U6.3 (VOUTB); also elsewhere on the board
DAC_C: U6.4 (VOUTC); also elsewhere on the board
DAC_D: U6.5 (VOUTD); also elsewhere on the board
FS_N: U1.122 (PA11), U14.15 (SPK_L)
FS_P: U1.123 (PA12), U14.16 (SPK_R)
GND: A1.P$1, A2.P$1, C27.2, C28.2, C29.2, C30.1, C32.2, C36.2, C39.2, C43.2, C47.2, C84.2, C85.2, C86.2, C90.2, J2.3 (GND), J2.5 (GND), J2.9 (GND_DETECT), J7.2, J22.P5 (GND), R1.2, R63.2, R64.1, U6.6 (GND), U12.1 (GND), U12.2 (A1), U12.3 (A2), U12.4 (GND), U12.7 (WP), U13.G1 (PAD), U13.G2 (PAD), U13.G3 (PAD), U13.G4 (PAD), U13.P6 (6), U13.S1 (1), U14.8 (S0), U14.14 (S2), U14.PAD (GND); also elsewhere on the board
I2C1_SCL: R6.1, U1.164 (PB6), U12.6 (SCL); also elsewhere on the board
I2C1_SDA: R7.1, U1.165 (PB7), U12.5 (SDA); also elsewhere on the board
MCO1: MCO1.P$1, U1.119 (PA8)
unnamed: R38.1, U14.26 (XI)
unnamed: R1.1, U14.24 (RBIAS)
unnamed: J22.P4 (ID), U14.23 (ID)
unnamed: R15.2, U14.22 (VBUS)
unnamed: C90.1, J7.1, R18.2, U6.7 (VREFIN)
unnamed: LED1.3 (RK), R12.2
unnamed: LED1.4 (GK), R13.2
unnamed: LED1.1 (BK), R14.2
unnamed: C42.2, Q1.1 (G), R20.1, R65.2
NRST: J2.10 (RESET); also elsewhere on the board
OSC32_IN: C27.1, U1.9 (PC14), X1.P$1
OSC32_OUT: C30.2, U1.10 (PC15), X1.P$2
PA15: U1.138 (PA15); also elsewhere on the board
PB4: R63.1, U1.162 (PB4), U14.27 (!RST_B)
PB8: U1.167 (PB8); also elsewhere on the board
PB9: U1.168 (PB9); also elsewhere on the board
PB14: R38.2, U1.94 (PB14)
PB15: U1.95 (PB15); also elsewhere on the board
PC6: U1.115 (PC6); also elsewhere on the board
PD0: U1.142 (PD0); also elsewhere on the board
PD1: U1.143 (PD1); also elsewhere on the board
PD3: U1.145 (PD3); also elsewhere on the board
PD4: U1.146 (PD4); also elsewhere on the board
PD6: U1.150 (PD6); also elsewhere on the board
PD7: U1.151 (PD7); also elsewhere on the board
PD8: U1.96 (PD8); also elsewhere on the board
PD9: U1.97 (PD9); also elsewhere on the board
PD10: U1.98 (PD10); also elsewhere on the board
PD11: U1.99 (PD11); also elsewhere on the board
PD12: U1.100 (PD12); also elsewhere on the board
PD13: R12.1, U1.101 (PD13)
PD14: R13.1, U1.104 (PD14)
PD15: R14.1, U1.105 (PD15)
PH3: R17.1, U6.9 (!SYNC); also elsewhere on the board
SDIO-PWR: R20.2, U1.121 (PA10)
SDIO-PWR-SWITCHED: C42.1, C43.1, Q1.3 (D), U13.P4 (4)
SDIO_CK-SPI3_MOSI: SPI3_MOSI.P$1, U1.141 (PC12), U6.8 (DIN), U13.P5 (5)
SDIO_CMD: U1.144 (PD2), U13.P3 (3)
SDIO_D0: R8.1, U1.117 (PC8), U13.P7 (7)
SDIO_D1: R9.1, U1.118 (PC9), U13.P8 (8)
SDIO_D2-SPI3_SCK: R10.1, SPI3_SCK.P$1, U1.139 (PC10), U6.10 (SCLK), U13.P1 (1)
SDIO_D3: R11.1, U1.140 (PC11), U13.P2 (2)
SD_DETECT: U1.116 (PC7), U13.S0 (0)
SHLD: C36.1, J22.P$1 (SHLD), J22.P$2 (SHLD), J22.P$3 (SHLD), J22.P$4 (SHLD)
SWDCK: J2.4 (SWDCLK), U1.137 (PA14)
SWDIO: J2.2 (SWDIO), U1.124 (PA13)
SWO: J2.6 (SWO), U1.161 (PB3)
UART4_RX: U1.41 (PA1); also elsewhere on the board
UART4_TX: U1.40 (PA0); also elsewhere on the board
ULPI_CK: U1.51 (PA5), U14.1 (CLK)
ULPI_D0: U1.47 (PA3), U14.3 (D0)
ULPI_D1: U1.56 (PB0), U14.4 (D1)
ULPI_D2: U1.57 (PB1), U14.5 (D2)
ULPI_D3: U1.79 (PB10), U14.6 (D3)
ULPI_D4: U1.80 (PB11), U14.7 (D4)
ULPI_D5: U1.92 (PB12), U14.9 (D5)
ULPI_D6: U1.93 (PB13), U14.10 (D6)
ULPI_D7: U1.163 (PB5), U14.13 (D7)
ULPI_DIR: U1.34 (PC2), U14.31 (DIR)
ULPI_NXT: U14.2 (NXT); also elsewhere on the board
ULPI_STP: U1.32 (PC0), U14.29 (STP)
USB_HS_N: J22.P2 (D-), U14.19 (DM/DP)
USB_HS_P: J22.P3 (D+), U14.18 (DP/DM)
V_USB: C32.1, J22.P1 (VCC), R15.1, U1.120 (PA9), V_USB.P$1; also elsewhere on the board

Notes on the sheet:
2mA
32.768kHz CLK
DAC
USB HS PHY
SWD Interface
SD Card Interface
EEPROM
*See Figure 8-1 USB3320 data sheet for application diagram
*Verify Rvbus value table 5-7 of USB3320 data sheet

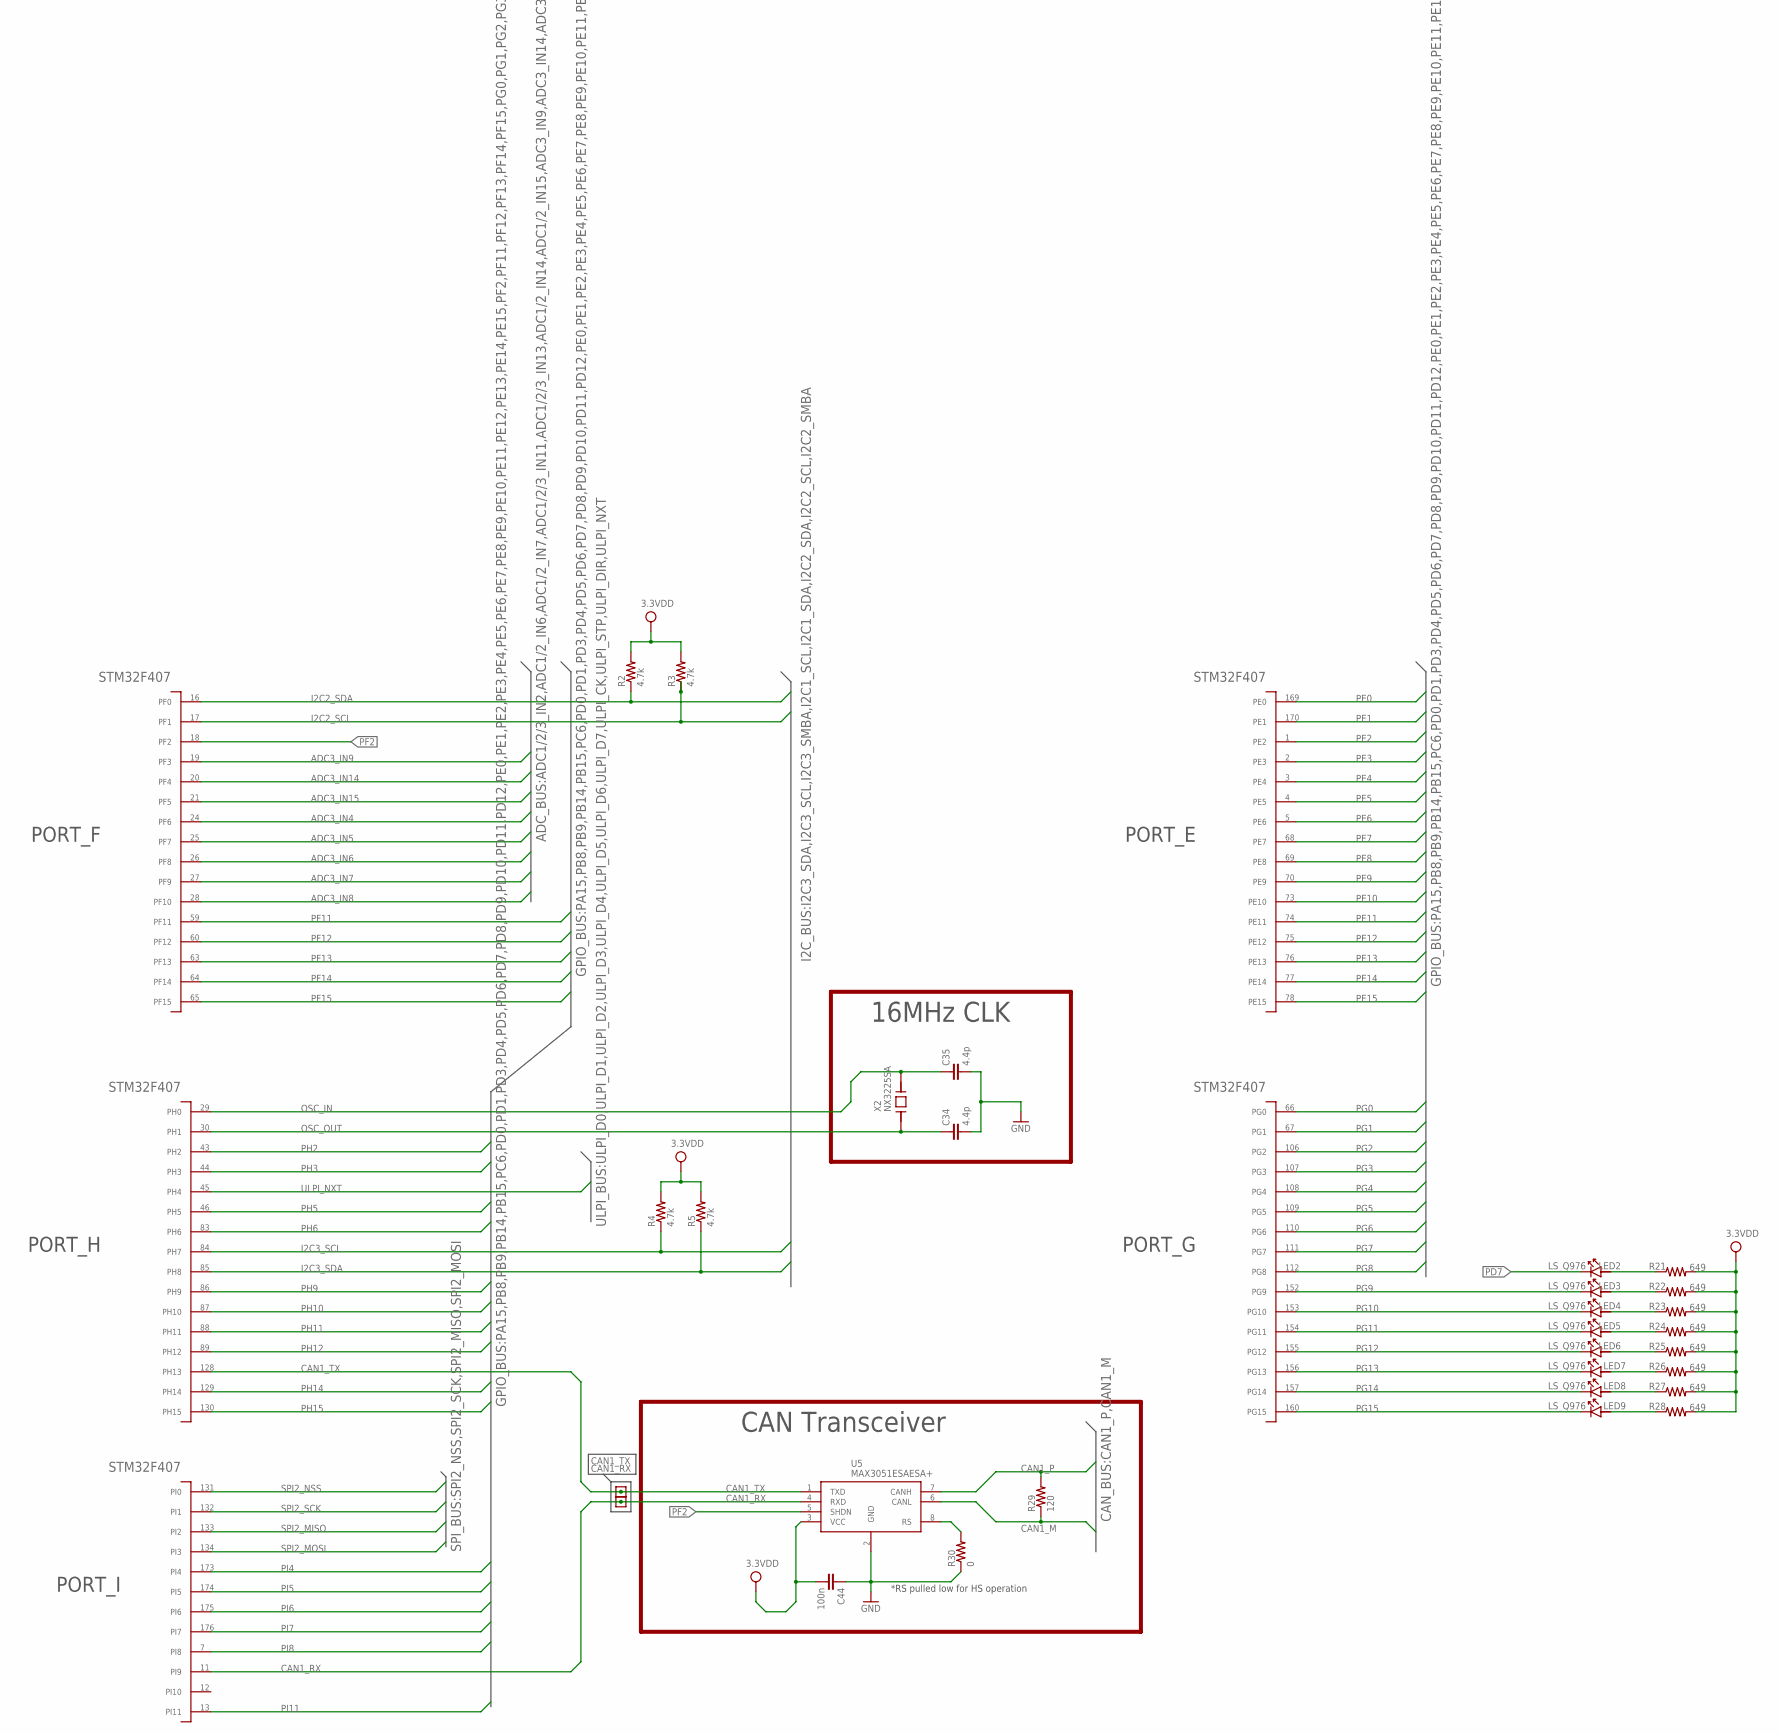
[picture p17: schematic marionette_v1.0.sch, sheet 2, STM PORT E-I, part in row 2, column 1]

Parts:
C34, C35: 4.4p; .0603-C
C44: 100n; .0603-C
CAN1_RX, CAN1_TX: TEST-POINT10MIL-TEST-POINT; 10MIL-TEST-POINT
LED2, LED3, LED4, LED5, LED6, LED7, LED8, LED9: LS_Q976; CHIPLED_0603
R2, R3, R4, R5: 4.7k; .0603-C
R21, R22, R23, R24, R25, R26, R27, R28: 649; .0603-C
R29: 120; .0603-C
R30: 0; .0603-C
U1: STM32F407; LQFP176
U5: MAX3051ESAESA+; SO8
X2: NX3225SA; DFN4SMD

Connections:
3.3VDD: C44.2, R2.2, R3.2, R4.2, R5.2, R21.2, R22.2, R23.2, R24.2, R25.2, R26.2, R27.2, R28.2, U5.3 (VCC); also elsewhere on the board
ADC3_IN4: U1.24 (PF6); also elsewhere on the board
ADC3_IN5: U1.25 (PF7); also elsewhere on the board
ADC3_IN6: U1.26 (PF8); also elsewhere on the board
ADC3_IN7: U1.27 (PF9); also elsewhere on the board
ADC3_IN8: U1.28 (PF10); also elsewhere on the board
ADC3_IN9: U1.19 (PF3); also elsewhere on the board
ADC3_IN14: U1.20 (PF4); also elsewhere on the board
ADC3_IN15: U1.21 (PF5); also elsewhere on the board
CAN1_M: R29.1, U5.6 (CANL); also elsewhere on the board
CAN1_P: R29.2, U5.7 (CANH); also elsewhere on the board
CAN1_RX: CAN1_RX.P$1, U1.11 (PI9), U5.4 (RXD)
CAN1_TX: CAN1_TX.P$1, U1.128 (PH13), U5.1 (TXD)
GND: C34.2, C35.2, C44.1, R30.1, U5.2 (GND); also elsewhere on the board
I2C2_SCL: R3.1, U1.17 (PF1); also elsewhere on the board
I2C2_SDA: R2.1, U1.16 (PF0); also elsewhere on the board
I2C3_SCL: R4.1, U1.84 (PH7); also elsewhere on the board
I2C3_SDA: R5.1, U1.85 (PH8); also elsewhere on the board
unnamed: R30.2, U5.8 (RS)
unnamed: LED2.A, R21.1
unnamed: LED3.A, R22.1
unnamed: LED4.A, R23.1
unnamed: LED5.A, R24.1
unnamed: LED6.A, R25.1
unnamed: LED7.A, R26.1
unnamed: LED8.A, R27.1
unnamed: LED9.A, R28.1
OSC_IN: C35.1, U1.29 (PH0), X2.P3
OSC_OUT: C34.1, U1.30 (PH1), X2.P2
PD7: LED2.C; also elsewhere on the board
PE0: U1.169 (PE0); also elsewhere on the board
PE1: U1.170 (PE1); also elsewhere on the board
PE2: U1.1 (PE2); also elsewhere on the board
PE3: U1.2 (PE3); also elsewhere on the board
PE4: U1.3 (PE4); also elsewhere on the board
PE5: U1.4 (PE5); also elsewhere on the board
PE6: U1.5 (PE6); also elsewhere on the board
PE7: U1.68 (PE7); also elsewhere on the board
PE8: U1.69 (PE8); also elsewhere on the board
PE9: U1.70 (PE9); also elsewhere on the board
PE10: U1.73 (PE10); also elsewhere on the board
PE11: U1.74 (PE11); also elsewhere on the board
PE12: U1.75 (PE12); also elsewhere on the board
PE13: U1.76 (PE13); also elsewhere on the board
PE14: U1.77 (PE14); also elsewhere on the board
PE15: U1.78 (PE15); also elsewhere on the board
PF2: U1.18 (PF2), U5.5 (SHDN)
PF11: U1.59 (PF11); also elsewhere on the board
PF12: U1.60 (PF12); also elsewhere on the board
PF13: U1.63 (PF13); also elsewhere on the board
PF14: U1.64 (PF14); also elsewhere on the board
PF15: U1.65 (PF15); also elsewhere on the board
PG0: U1.66 (PG0); also elsewhere on the board
PG1: U1.67 (PG1); also elsewhere on the board
PG2: U1.106 (PG2); also elsewhere on the board
PG3: U1.107 (PG3); also elsewhere on the board
PG4: U1.108 (PG4); also elsewhere on the board
PG5: U1.109 (PG5); also elsewhere on the board
PG6: U1.110 (PG6); also elsewhere on the board
PG7: U1.111 (PG7); also elsewhere on the board
PG8: U1.112 (PG8); also elsewhere on the board
PG9: LED3.C, U1.152 (PG9)
PG10: LED4.C, U1.153 (PG10)
PG11: LED5.C, U1.154 (PG11)
PG12: LED6.C, U1.155 (PG12)
PG13: LED7.C, U1.156 (PG13)
PG14: LED8.C, U1.157 (PG14)
PG15: LED9.C, U1.160 (PG15)
PH2: U1.43 (PH2); also elsewhere on the board
PH3: U1.44 (PH3); also elsewhere on the board
PH5: U1.46 (PH5); also elsewhere on the board
PH6: U1.83 (PH6); also elsewhere on the board
PH9: U1.86 (PH9); also elsewhere on the board
PH10: U1.87 (PH10); also elsewhere on the board
PH11: U1.88 (PH11); also elsewhere on the board
PH12: U1.89 (PH12); also elsewhere on the board
PH14: U1.129 (PH14); also elsewhere on the board
PH15: U1.130 (PH15); also elsewhere on the board
PI4: U1.173 (PI4); also elsewhere on the board
PI5: U1.174 (PI5); also elsewhere on the board
PI6: U1.175 (PI6); also elsewhere on the board
PI7: U1.176 (PI7); also elsewhere on the board
PI8: U1.7 (PI8); also elsewhere on the board
PI11: U1.13 (PI11); also elsewhere on the board
SPI2_MISO: U1.133 (PI2); also elsewhere on the board
SPI2_MOSI: U1.134 (PI3); also elsewhere on the board
SPI2_NSS: U1.131 (PI0); also elsewhere on the board
SPI2_SCK: U1.132 (PI1); also elsewhere on the board
ULPI_NXT: U1.45 (PH4); also elsewhere on the board

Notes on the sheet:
*RS pulled low for HS operation
16MHz CLK
CAN Transceiver

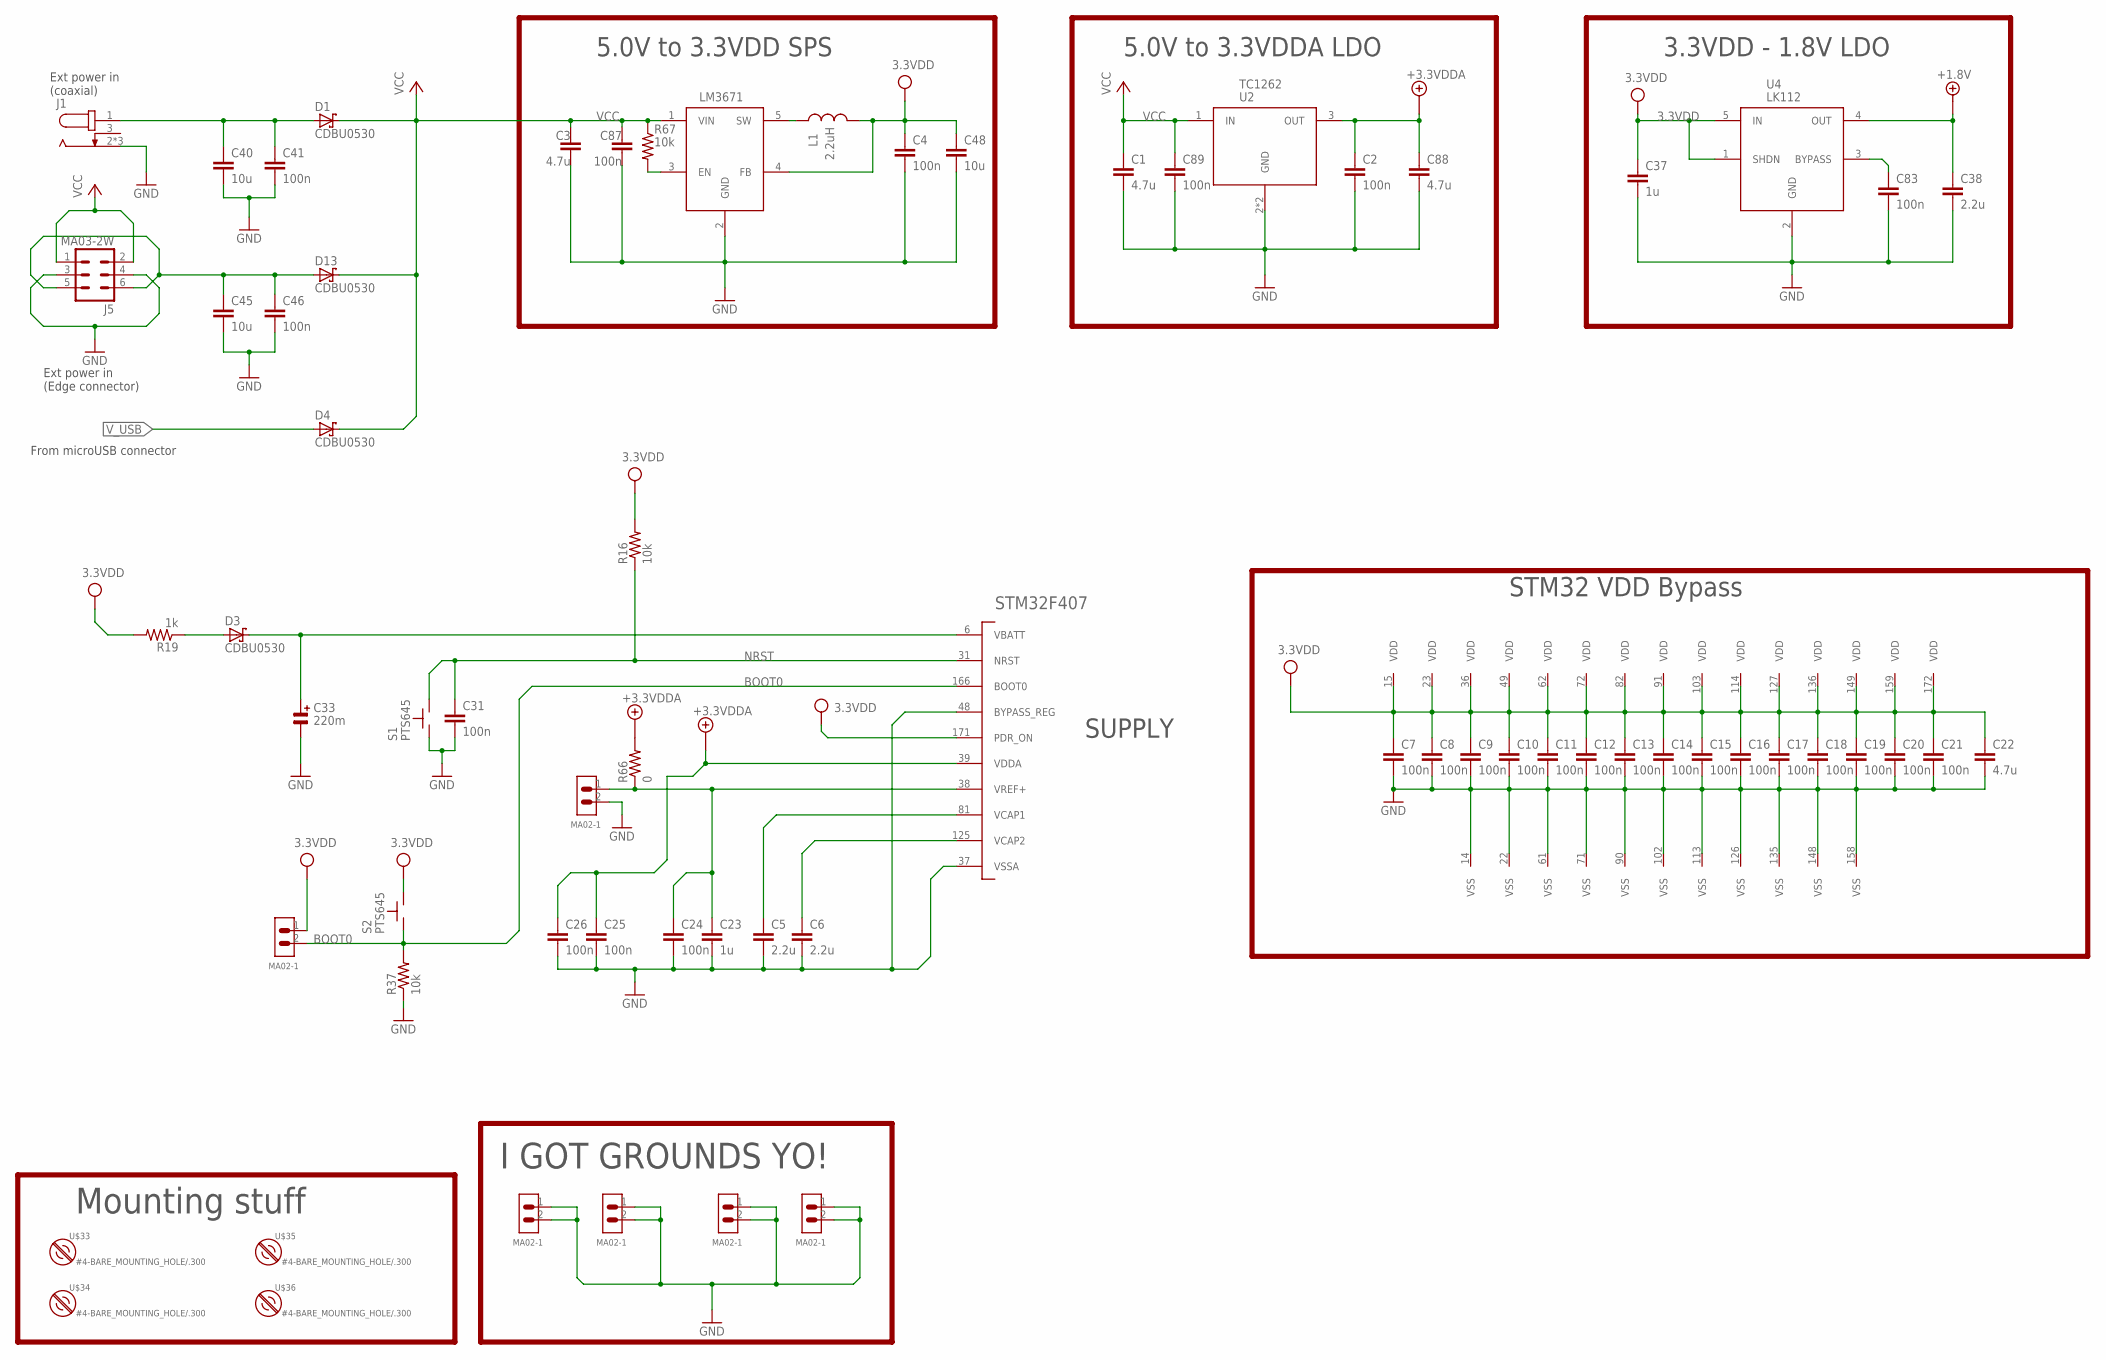
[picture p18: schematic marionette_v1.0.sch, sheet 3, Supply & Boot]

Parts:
C1, C3, C22, C88: 4.7u; .0805-C-NOSILK
C2, C4, C7, C8, C9, C10, C11, C12, C13, C14, C15, C16, C17, C18, C19, C20, C21, C24, C25, C26, C31, C41, C46, C83, C87, C89: 100n; .0603-C
C5, C6, C38: 2.2u; .0603-C
C23, C37: 1u; .0603-C
C33: 220m; SCAP
C40, C45, C48: 10u; .0805-C-NOSILK
D1, D3, D4, D13: CDBU0530; SOD-523F
J1: JACK-PLUG; MALE_JACK
J4, J17, J18, J19, J20, J23: MA02-1
J5: MA03-2W
L1: 2.2uH; CDRH2D14
R16, R37, R67: 10k; .0603-C
R19: 1k; .0603-C
R66: 0; .0603-C
S1, S2: PTS645; SMT
U1: STM32F407; LQFP176
U2: TC1262; SOT223
U3: LM3671; SOT23-5L
U4: LK112; SOT23-5
U$33, U$34, U$35, U$36: #4-BARE_MOUNTING_HOLE/.300; #4/.300-BARE+STD_NUT_OR_STAR_WASHER

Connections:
3.3VDD: C4.1, C7.1, C8.1, C9.1, C10.1, C11.1, C12.1, C13.1, C14.1, C15.1, C16.1, C17.1, C18.1, C19.1, C20.1, C21.1, C22.1, C37.1, C48.1, J23.1, L1.2, R16.2, R19.2, S2.3, S2.4, U1.15 (VDD), U1.23 (VDD), U1.36 (VDD), U1.49 (VDD), U1.62 (VDD), U1.72 (VDD), U1.82 (VDD), U1.91 (VDD), U1.103 (VDD), U1.114 (VDD), U1.127 (VDD), U1.136 (VDD), U1.149 (VDD), U1.159 (VDD), U1.171 (PDR_ON), U1.172 (VDD), U3.4 (FB), U4.1 (SHDN), U4.5 (IN); also elsewhere on the board
+1.8V: C38.1, U4.4 (OUT); also elsewhere on the board
+3.3VDDA: C2.1, C25.1, C26.1, C88.1, R66.2, U1.39 (VDDA), U2.3 (OUT); also elsewhere on the board
BOOT0: J23.2, R37.2, S2.1, S2.2, U1.166 (BOOT0)
GND: C1.2, C2.2, C3.2, C4.2, C5.2, C6.2, C7.2, C8.2, C9.2, C10.2, C11.2, C12.2, C13.2, C14.2, C15.2, C16.2, C17.2, C18.2, C19.2, C20.2, C21.2, C22.2, C23.2, C24.2, C25.2, C26.2, C31.2, C33.N, C37.2, C38.2, C40.2, C41.2, C45.2, C46.2, C48.2, C83.2, C87.2, C88.2, C89.2, J1.2, J1.P$1 (2), J1.P$2 (2), J4.2, J5.3, J5.4, J17.1, J17.2, J18.1, J18.2, J19.1, J19.2, J20.1, J20.2, R37.1, S1.1, S1.2, U1.14 (VSS), U1.22 (VSS), U1.37 (VSSA), U1.48 (BYPASS_REG), U1.61 (VSS), U1.71 (VSS), U1.90 (VSS), U1.102 (VSS), U1.113 (VSS), U1.126 (VSS), U1.135 (VSS), U1.148 (VSS), U1.158 (VSS), U2.2 (GND), U2.4 (GND), U3.2 (GND), U4.2 (GND); also elsewhere on the board
unnamed: R67.2, U3.3 (EN)
unnamed: L1.1, U3.5 (SW)
unnamed: C83.1, U4.3 (BYPASS)
unnamed: D3.P$1 (A), R19.1
unnamed: C6.1, U1.125 (VCAP2)
unnamed: C5.1, U1.81 (VCAP1)
NRST: C31.1, R16.1, S1.3, S1.4, U1.31 (NRST); also elsewhere on the board
VBATT: C33.P, D3.P$2 (C), U1.6 (VBATT)
VCC: C1.1, C3.1, C87.1, C89.1, D1.P$2 (C), D4.P$2 (C), D13.P$2 (C), J5.1, J5.2, R67.1, U2.1 (IN), U3.1 (VIN)
VEXT-COAX: C40.1, C41.1, D1.P$1 (A), J1.1
VEXT-ECOD: C45.1, C46.1, D13.P$1 (A), J5.5, J5.6
VREF+: C23.1, C24.1, J4.1, R66.1, U1.38 (VREF+)
V_USB: D4.P$1 (A); also elsewhere on the board

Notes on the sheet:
STM32 VDD Bypass
5.0V to 3.3VDDA LDO
5.0V to 3.3VDD SPS
3.3VDD - 1.8V LDO
Mounting stuff
Ext power in (coaxial)
Ext power in (Edge connector)
I GOT GROUNDS YO!
From microUSB connector

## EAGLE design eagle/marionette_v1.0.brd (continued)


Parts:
D15, D16, D17, D18, D19, D20, D21, D22, D24, D25, D26, D27: ESD8008; UFDFN-14
J3, J12, J13, J15, J16, J24: MA02-2W
J8, J21: MA04-2W
J9, J11, J14: MA10-2W
SCL: TEST-POINT10MIL-TEST-POINT; 10MIL-TEST-POINT
SDA: TEST-POINT10MIL-TEST-POINT; 10MIL-TEST-POINT

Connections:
3.3VDD: J3.3, J8.7, J8.8, J9.1, J9.2, J11.1, J11.2, J12.3, J13.3, J14.1, J14.2, J15.3, J16.3; also elsewhere on the board
CAN1_M: D25.P7 (I/O7), J12.4; also elsewhere on the board
CAN1_P: D25.P6 (I/06), J12.2; also elsewhere on the board
GND: D15.GND@1 (GND), D15.GND@2 (GND), D15.GND@3 (GND), D15.GND@4 (GND), D15.GND@5 (GND), D15.GND@6 (GND), D16.GND@1 (GND), D16.GND@2 (GND), D16.GND@3 (GND), D16.GND@4 (GND), D16.GND@5 (GND), D16.GND@6 (GND), D17.GND@1 (GND), D17.GND@2 (GND), D17.GND@3 (GND), D17.GND@4 (GND), D17.GND@5 (GND), D17.GND@6 (GND), D17.P1 (I/O1), D17.P3 (I/O3), D18.GND@1 (GND), D18.GND@2 (GND), D18.GND@3 (GND), D18.GND@4 (GND), D18.GND@5 (GND), D18.GND@6 (GND), D19.GND@1 (GND), D19.GND@2 (GND), D19.GND@3 (GND), D19.GND@4 (GND), D19.GND@5 (GND), D19.GND@6 (GND), D19.P3 (I/O3), D19.P5 (I/05), D20.GND@1 (GND), D20.GND@2 (GND), D20.GND@3 (GND), D20.GND@4 (GND), D20.GND@5 (GND), D20.GND@6 (GND), D21.GND@1 (GND), D21.GND@2 (GND), D21.GND@3 (GND), D21.GND@4 (GND), D21.GND@5 (GND), D21.GND@6 (GND), D21.P4 (I/04), D21.P6 (I/06), D22.GND@1 (GND), D22.GND@2 (GND), D22.GND@3 (GND), D22.GND@4 (GND), D22.GND@5 (GND), D22.GND@6 (GND), D24.GND@1 (GND), D24.GND@2 (GND), D24.GND@3 (GND), D24.GND@4 (GND), D24.GND@5 (GND), D24.GND@6 (GND), D25.GND@1 (GND), D25.GND@2 (GND), D25.GND@3 (GND), D25.GND@4 (GND), D25.GND@5 (GND), D25.GND@6 (GND), D26.GND@1 (GND), D26.GND@2 (GND), D26.GND@3 (GND), D26.GND@4 (GND), D26.GND@5 (GND), D26.GND@6 (GND), D26.P4 (I/04), D26.P6 (I/06), D27.GND@1 (GND), D27.GND@2 (GND), D27.GND@3 (GND), D27.GND@4 (GND), D27.GND@5 (GND), D27.GND@6 (GND), J3.1, J8.1, J8.2, J9.19, J9.20, J11.19, J11.20, J12.1, J13.1, J14.19, J14.20, J15.1, J16.1; also elsewhere on the board
I2C1_SCL: D25.P3 (I/O3), J3.4, SCL.P$1; also elsewhere on the board
I2C1_SDA: D25.P2 (I/O2), J3.2, SDA.P$1; also elsewhere on the board
I2C2_SCL: D22.P7 (I/O7), J15.2; also elsewhere on the board
I2C2_SDA: D22.P8 (I/O8), J15.4; also elsewhere on the board
I2C3_SCL: D27.P1 (I/O1), J16.2; also elsewhere on the board
I2C3_SDA: D27.P2 (I/O2), J16.4; also elsewhere on the board
PA15: D26.P8 (I/O8), J14.5; also elsewhere on the board
PB8: D15.P8 (I/O8), J9.12; also elsewhere on the board
PB9: D15.P7 (I/O7), J9.11; also elsewhere on the board
PB15: D18.P1 (I/O1), J14.14; also elsewhere on the board
PC6: D17.P2 (I/O2), J14.8; also elsewhere on the board
PD0: D16.P5 (I/05), J9.17; also elsewhere on the board
PD1: D16.P4 (I/04), J9.15; also elsewhere on the board
PD3: D16.P3 (I/O3), J9.16; also elsewhere on the board
PD4: D16.P2 (I/O2), J9.13; also elsewhere on the board
PD6: D16.P1 (I/O1), J9.14; also elsewhere on the board
PD8: D18.P2 (I/O2), J14.13; also elsewhere on the board
PD9: D18.P3 (I/O3), J14.16; also elsewhere on the board
PD10: D18.P4 (I/04), J14.15; also elsewhere on the board
PD11: D18.P5 (I/05), J14.17; also elsewhere on the board
PD12: D18.P6 (I/06), J14.18; also elsewhere on the board
PE0: D15.P6 (I/06), J9.10; also elsewhere on the board
PE1: D27.P7 (I/O7), J9.3; also elsewhere on the board
PE2: D27.P8 (I/O8), J9.4; also elsewhere on the board
PE3: D15.P1 (I/O1), J9.6; also elsewhere on the board
PE4: D15.P2 (I/O2), J9.5; also elsewhere on the board
PE5: D15.P3 (I/O3), J9.8; also elsewhere on the board
PE6: D15.P4 (I/04), J9.7; also elsewhere on the board
PE7: D20.P4 (I/04), J11.11; also elsewhere on the board
PE8: D20.P5 (I/05), J11.13; also elsewhere on the board
PE9: D20.P6 (I/06), J11.14; also elsewhere on the board
PE10: D20.P7 (I/O7), J11.15; also elsewhere on the board
PE11: D20.P8 (I/O8), J11.16; also elsewhere on the board
PE12: D26.P1 (I/O1), J11.18; also elsewhere on the board
PE13: D26.P2 (I/O2), J11.17; also elsewhere on the board
PE14: D26.P3 (I/O3), J14.4; also elsewhere on the board
PE15: D26.P5 (I/05), J14.3; also elsewhere on the board
PF11: D19.P4 (I/04), J11.5; also elsewhere on the board
PF12: D19.P6 (I/06), J11.6; also elsewhere on the board
PF13: D19.P7 (I/O7), J11.7; also elsewhere on the board
PF14: D19.P8 (I/O8), J11.8; also elsewhere on the board
PF15: D20.P1 (I/O1), J11.10; also elsewhere on the board
PG0: D20.P2 (I/O2), J11.9; also elsewhere on the board
PG1: D20.P3 (I/O3), J11.12; also elsewhere on the board
PG2: D18.P7 (I/O7), J21.1; also elsewhere on the board
PG3: D18.P8 (I/O8), J21.2; also elsewhere on the board
PG4: D21.P1 (I/O1), J21.4; also elsewhere on the board
PG5: D21.P2 (I/O2), J21.3; also elsewhere on the board
PG6: D21.P3 (I/O3), J21.6; also elsewhere on the board
PG7: D21.P5 (I/05), J21.5; also elsewhere on the board
PG8: D17.P8 (I/O8), J14.12; also elsewhere on the board
PH2: D19.P1 (I/O1), J11.3; also elsewhere on the board
PH5: D19.P2 (I/O2), J11.4; also elsewhere on the board
PH6: D26.P7 (I/O7), J14.6; also elsewhere on the board
PH9: D17.P4 (I/04), J14.7; also elsewhere on the board
PH10: D17.P5 (I/05), J14.9; also elsewhere on the board
PH11: D17.P6 (I/06), J14.10; also elsewhere on the board
PH12: D17.P7 (I/O7), J14.11; also elsewhere on the board
PH14: D21.P7 (I/O7), J21.8; also elsewhere on the board
PH15: D21.P8 (I/O8), J21.7; also elsewhere on the board
PI4: D27.P6 (I/06), J24.4; also elsewhere on the board
PI5: D27.P5 (I/05), J24.3; also elsewhere on the board
PI6: D27.P4 (I/04), J24.2; also elsewhere on the board
PI7: D27.P3 (I/O3), J24.1; also elsewhere on the board
PI8: D15.P5 (I/05), J9.9; also elsewhere on the board
PI11: D16.P7 (I/O7), J9.18; also elsewhere on the board
SPI2_MISO: D24.P3 (I/O3), J8.4; also elsewhere on the board
SPI2_MOSI: D24.P1 (I/O1), J8.3; also elsewhere on the board
SPI2_NSS: D24.P8 (I/O8), J8.5; also elsewhere on the board
SPI2_SCK: D24.P6 (I/06), J8.6; also elsewhere on the board
UART4_RX: D22.P2 (I/O2), J13.4; also elsewhere on the board
UART4_TX: D22.P1 (I/O1), J13.2; also elsewhere on the board

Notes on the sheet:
mBUS
SPI
I2C
UART
CAN
GPIO-BUS


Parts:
C49, C50, C51, C52, C53, C54, C57, C58, C59, C60, C61, C62, C63, C64, C65, C66, C67, C68, C69, C70, C71, C72, C73, C74, C75, C76, C77, C78, C79, C80: 1n; .0603-C
C55, C56, C81, C82: 1u; .0603-C
D23: ESD8008; UFDFN-14
J6: MA03-2W
J10: MA10-2W
R31, R32, R33, R34, R35, R36, R39, R40, R41, R42, R43, R44, R45, R46, R47, R48, R49, R50, R51, R52, R53, R54, R55, R56, R57, R58, R59, R60, R61, R62: 7.5k; .0603-C
U7, U8, U9, U10: LVM344; SOIC-14
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

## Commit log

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2015-02-07 added schottky diodes
    [marionette.sch]
2015-02-07 Replaced SPS symbol with new version
    [marionette.sch]
2015-02-07 Added capacitors to supply sheet
    [marionette.sch]
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2015-02-07 small changes
    [marionette.sch]
2015-02-08 Modified USB3318 symbol
    [marionette.sch]
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2015-02-08 Added USB ULPI and SWD components
    [marionette.sch]
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2015-02-12 Removed ABS07L.lbr, this crystal did not have enough gain margin. Added VDDA and VDD symbols to marionette.sch
    [marionette.sch]
2015-02-12 Added connection to SDIO_BUS
    [marionette.sch]
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2015-02-12 Added ADC bus
    [marionette.sch]
2015-02-12 library housekeeping. Added U prefix to devices
    [marionette.sch]
2015-02-12 added GPIO bus
    [marionette.sch]
2015-02-12 started board layout
    [marionette.brd]
2015-02-12 added labeling to some nets
    [marionette.sch]
2015-02-13 Added 20pin connectors
    [marionette.brd, marionette.sch]
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2015-02-13 Added micro USB connectors
    [marionette.brd, marionette.sch]
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2015-02-14 Replaced resistors and capacitors with Marionette library components
    [marionette.brd, marionette.sch]
2015-02-15 Updatede schematic and board layout
    [marionette.sch]
2015-02-15 Updated schematic data buses
    [marionette.sch]
2015-02-15 Added connections to the EDGE CONNECTOR OF DEATH!!!!!!!!!!!!!
    [marionette.brd, marionette.sch]
2015-02-15 Updated board layout
    [marionette.brd]
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2015-02-17 Added RGB led and resistors
    [marionette.brd, marionette.sch]
2015-02-17 library update/maintinence and added pullup and pulldown resisters
    [marionette.brd, marionette.sch]
2015-02-17 Added super cap and circuitry
    [marionette.brd, marionette.sch]
2015-02-17 Added 16Mhz clock to schematic
    [marionette.sch]
2015-02-17 Edited device prefix
    [marionette.sch]
2015-02-17 Added notes and changes from rough draft review
    [marionette.brd, marionette.sch]
2015-02-17 Added SD detect, fixed some gpio stuff, added some other labels
    [marionette.sch]
2015-02-19 Removed the female edge connectors and added angle male headers
    [marionette.sch]
2015-02-19 Added 1.8V LDO and symbol
    [marionette.sch]
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2015-02-20 Added header connections for boot0 and boot1
    [marionette.sch]
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2015-02-21 Edited Scap symbol, added 1x3 male headder, created 12bit DAC library, edited marionette schematic
    [marionette.sch]
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2015-02-23 Connected RGB LEDs to PWM GPIOs
    [marionette.sch]
2015-02-24 finished all connections, schematic ready for review
    [marionette.brd, marionette.sch]
2015-02-24 Changed footprint of parts, the pins should no longer be shorted
    [marionette.brd, marionette.sch]
2015-02-24 Changed VDD and VSS pin direction from sup to pwr
    [marionette.sch]
2015-02-24 replaced high density 0.05" header with 0.1" header.
    [marionette.brd, marionette.sch]
2015-03-01 Cleaned up schematic and edited prefix of male header
    [marionette.brd, marionette.sch]
2015-03-01 Replaced DAC chip on marionette
    [marionette.brd, marionette.sch]
2015-03-01 Replaced 32.768kHz crystal and updated crystal symbol
    [marionette.brd, marionette.sch]
2015-03-02 replaced 32kHz crystal loading caps
    [marionette.brd, marionette.sch]
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2015-03-02 Added CAN tranceiver
    [marionette.brd, marionette.sch]
2015-03-02 Added labeling
    [marionette.sch]
2015-03-03 Added test pads, mounting holes, and ground headders
    [marionette.brd, marionette.sch]
2015-03-03 Added some test points
    [marionette.brd, marionette.sch]
2015-03-04 added connected for ECOD power in
    [marionette.brd, marionette.sch]
2015-03-04 Added ECOD power connector, edited header footprints and adjusted some layout
    [marionette.brd, marionette.sch]
2015-03-05 Updated right angle header components. Started component placement.
    [marionette.brd, marionette.sch]
2015-03-05 placed some parts, looks good
    [marionette.brd, marionette.sch]
2015-03-06 added 0 ohm resistor to CAN Rs
    [marionette.brd, marionette.sch]
2015-03-07 Reduced net crossover for ADC and GPIO
    [marionette.brd, marionette.sch]
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2015-04-19 Replaced C42 - 0603 package with 0402 package size 0603 package size is not available
    [marionette.brd, marionette.sch]
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2015-04-21 fixed the 0ohm resistor to ULPI
    [marionette.brd, marionette.sch]
2015-04-21 fixed boot0 switch for DFU
    [marionette.brd, marionette.sch]
2015-04-21 Fixed text size and ratio for tsilk
    [marionette.brd]
2015-04-21 now I really fixed switch for DFU
    [marionette.brd, marionette.sch]
2015-04-21 Approved ERC and DRC errors that werent really errors (YAY!)
    [marionette.brd, marionette.sch]
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2015-04-27 Added replacement 1.8V/3.3V LDO and associated bypass caps
    [marionette.brd]
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2015-05-02 Uh... some changes. Sorry Jeff. I realized I hadn't passed the layout by our 'customers', specifically Chris and a few other mfg engineers, and they wanted the spare headers wrapped around the edge o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
    - Moved BOOT0 and BOOT0 jumper to near board edge (for mezannine stacking). Also cleaned up Jumper (only need to pull high).
    - Removed BOOT1 jumper - we don't need it. We'll never (HA!) boot out of SRAM.
    - Moved LED towards edge of board (for mezannine stacking)
    - Replaced all 0402 packages with 0603s.
    - Added un-invoked spare op-amp as a fo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
    [marionette.brd, marionette.sch]
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2015-05-03 Added note about C34 and C35. Need to find replacement part. Consider changing package to 0402.
    [mBom.xlsx]
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2015-05-05 Did more on the board:
    - ZERO OHM RESISTOR ON JUMPERS
    - Fixed power and bypass cap to on-board EEPROM
    - Added 10 uF cap to uSD card.
    - Added more bypass to power supplies (0805 10u and 0603 100n to various supplies)
    [marionette.brd, marionette.sch]
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2015-05-06 Forgot some grounding points by TVS, so I added them and updated the Gerbers. Also fixed the OSH Park CAM file which didn't specify Excellon drill device.
    [marionette.brd, marionette.drills.xln]
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2015-05-08 Accidently had 0603metric components instead of 0603in components. Fixed this and finished mouser partnumbers as well.
    [mBom.xlsx]
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2015-05-10 Correctly connected 32.768kHz clock connection. This changed the gpio that was connected to SDIO-PWR. Minor changes to the schematic and layout. Also made some minor changes to the silk screen
    [marionette.brd, marionette.sch]
2015-05-10 New gerbers for osc32.768kHz fix
    [marionette.drills.xln]
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2015-05-19 fixed label error for PD11 on sheet4 - it now is correct Shifted Net labels for gpio up by .01in - They should be easier to read
    [marionette.sch]
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2015-06-10 Corrected 3.3V SPS inductor connections. The SPS is now correct and will no longer need a mod wire. This fix is necessary as per issue #5 in the hardware repo.
    [marionette.brd, marionette.sch]
2015-06-19 Added correct CAN transceiver footprint as per marionette-hardware issue #3
    [marionette.brd, marionette.sch]
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2015-07-02 Added updated DAC footprint and fixed routing as per issue #11
    [marionette.brd, marionette.sch]
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2015-07-15 Verified STM32F427 pinout and started swapping in new device into schematic with slightly rearranged ports for auxiliary and supply and control functions
    [marionette.brd, marionette.sch]
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2015-09-08 Added the V3.3A/V3.3D shorting - crowbar circuit.
    [marionette.brd, marionette.sch]
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2015-12-01 artwork mostly arranged. Moved fb components around in the switching power supply to minimize ground loop problems
    [marionette.brd, marionette.sch]
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2015-12-09 still a few loose ends
    [marionette.brd, marionette.sch]
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2015-12-19 Caught some problems with schematic while making BOM. The MIC5305 in fixed output voltages is not stocked at digikey (or mouser), so had to find some other fixed LDOs to substitute. Bottom line, neve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
    [marionette.sch]
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2015-12-19 Replaced a PFET on the SD card with the AO3419, but had to delete and add component even though same package, so board changed slightly slightly, but passes DRC.
    [marionette.brd]
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2016-05-23 Marionette rough draft. All signals routed, no DRC errors. Left to do: optomize power routing (maybe planes?) and clean up silk screen.
    [marionette.brd, marionette.sch]
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2016-09-08 Changed the hole size on the 20 pin and 40 pin connectors from 0.8mm to 0.914mm which will correctly receive the 0.64mm square pins. I chose 0.914mm which is 36mil from the sunstone drill rack. Going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
    [marionette.brd, marionette.sch]
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2016-12-07 imon board passes 6mil DRC. The gain on the 4th order Bessel filter is probably wrong and needs to be redone, but the layout is ready for review
    [imon.brd, imon.sch]
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2018-03-29 Version 2.2 of the project. Schematic is now feaure complete. Includes up to 40V supply input and battery backup capabilities. Lots and lots of small fixes, too.
    [marionette.brd, marionette.sch]
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2018-03-29 Updated terminal block and solved some DRCs. Solved more Github issues.
    [marionette.brd, marionette.sch]
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2021-01-21 Quick DRC fixes on board before fab at OSH Park.
    [marionette.brd]

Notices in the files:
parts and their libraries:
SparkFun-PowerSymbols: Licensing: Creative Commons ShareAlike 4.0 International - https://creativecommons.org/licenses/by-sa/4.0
